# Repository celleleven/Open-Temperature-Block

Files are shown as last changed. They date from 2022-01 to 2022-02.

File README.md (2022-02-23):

<p align="center">
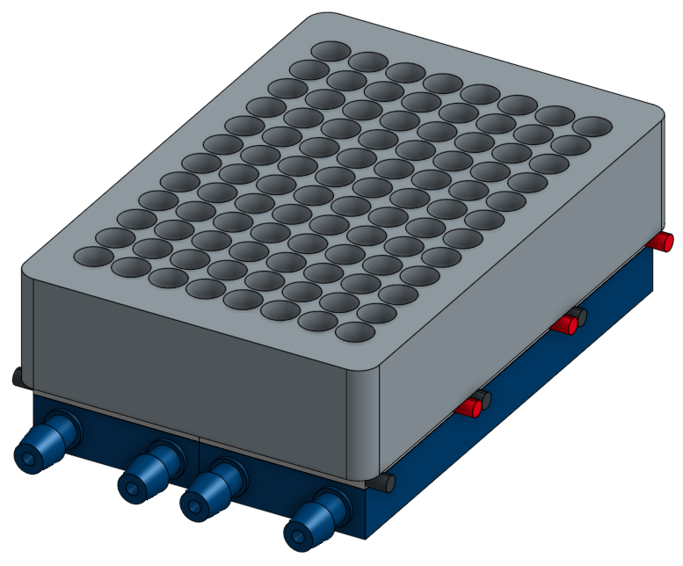
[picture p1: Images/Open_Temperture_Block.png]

</p>

# Open Temperature Block

_**TL;DR**_ This guide shows the process for engineering, fabrication, and operating of the OTB (Open Temperature Block).  The OTB is a bench tool for controlling the temperature of DIY biological experiments to include and is not limited to PCR, heat shock, hibernation, and incubation.  

### Background

## Engineering Design Process

	1.	Define the Problem:

The goal is to create a DIY, open-source, heating and cooling device for use in biological experiments.  The DIY portion of this device will be assembled using basic tools. Being open-source allows for revision, evolution, and free dissemination.  The heating control will allow for PCR reactions, heat shock experiments, incubation, and hibernation.

	2.	Identify Constraints:

| Name | Parameters |
| ----- | -----|
| Size | Microplate footprint (127.76 mm x 85.48 mm)|
| Weight | For shipping lighter is better |
| Cost | < $1000 USD (Competitor range: $900 <-> $20K, Average $5k )
| Power | 120VAC and 240VAC input
| Temperature Range |  ≤ 3°C to ≥ 100°C for a duration of < 30 Minutes |
|Componets| Readily sourced; electronics, hardware, microcontroller|
| Decibels | 60 decibels
| Water Tight | Does not leak
| Geometry | Rectangular
| Cleanability | Allows for cleaning.
| Assembly | Uses standard hex screws.

	3.	Brainstorm:

  | Idea | Pro | Con |
  | ----- | -----| ----- |
  |Peltier (TEC)| Cost-effective, heats and cools, small size| Uses a lot of power to remove heat.
  |Heat Element| Cost-effective, any size filament|  Doesn't cool
  |Compressor heat exchanger|Power Efficient|Expensive, Slow, not DIY.

	4.	Select promising solution:

The engineered solution will use a Thermal Electric Cooler (TEC) and a heat exchanger.  To create the OTB there will be three systems; power, data, and water-heat.

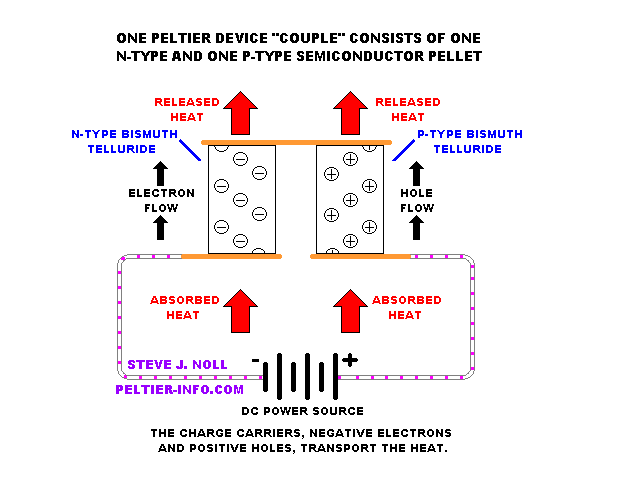
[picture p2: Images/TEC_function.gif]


The OTB is powered by a 12V 17AMP power supply. This will power the Peltier, fans, pump, and a voltage regulator will step down the 12V to 5V for the microcontroller.

The OTB data system is broken into device logic and external control. Device logic describes the microcontroller interaction with the Peltier, Temperature Probes, input devices. To accurately control the Peltier the microcontroller supplies a PWM signal to the high-power motor controller. This will change the electrical duty cycle allowing for precise Peltier control. The microcontroller samples temperatures from two thermistors.  One thermistor is located on the heat block and the other is attached to the heat exchanger.  These values will provide the logic needed to safely control the heat and cooling operations. External control consists of an I2C slave data line, display with buttons, and Wifi. The I2C data line allows for sending and receiving data from a Master I2C device. The display consists of an OLED display and four buttons.  The OLED in conjunction with the buttons allows the user to navigate through menus, and execute functions. Lastly, the Wifi provides a wireless gateway to Communicate with the OTB via a web page and RESTapi.

The water-heat system consists of a water block, pump, fan, and radiator.  In the heating phase, the microcontroller sends positive voltage to the Peltier.  In the cooling phase, the microcontroller sends a negative voltage to the Peltier.  Durning all heating and cooling operations the pump is moving water through the water block, through the tubing, to the radiator, and back to the water block.  The radiator uses an electric fan to blow air over the fins and exchange heat to the environment.

**Sketch (Free Body Diagram):**

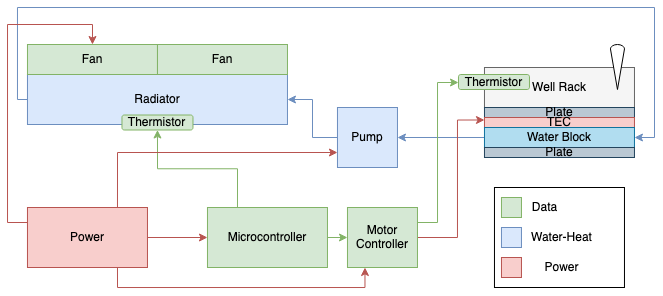
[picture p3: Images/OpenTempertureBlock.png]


<br><br>
MATH:

<!--
I have a circular track on this track there is a mine-cart.  The mine-cart picks up a payload (ore) at the vein.  The payload moves to the collector are emptied and repeats.  The mine-cart has a continuous speed around the track.  There is a rate the ore can be loaded into the mine cart, and there is a rate the ore can be removed to the collector.

If I cut the track in half, and start at the vein.
-->

	5.	Prototype

### Temperture Block
 <br>Parametric Model.

 <br>Version 1<br>

### Heat Exchanger and Power Train
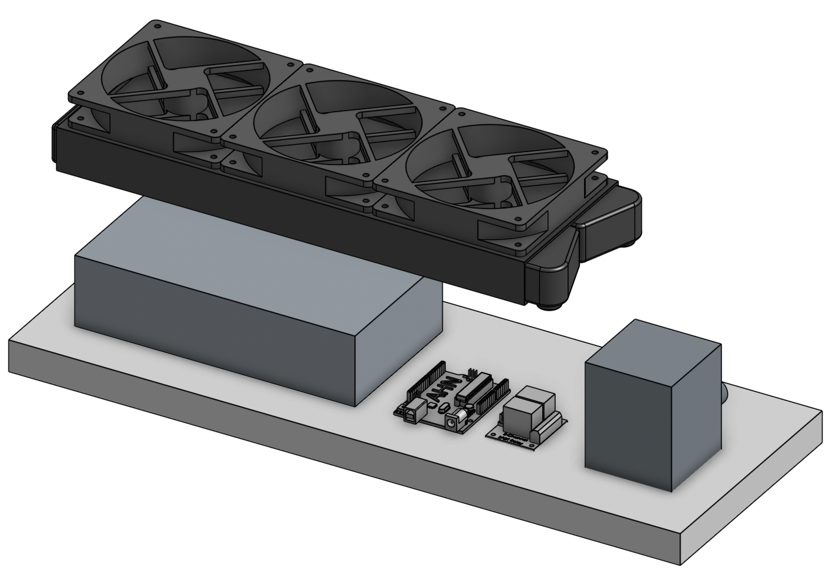
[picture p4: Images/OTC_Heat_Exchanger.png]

<br>Parametric Model.<br>


<br>Version 1<br>

### Logic Controller


<br>Version 1<br>

### Software Interface

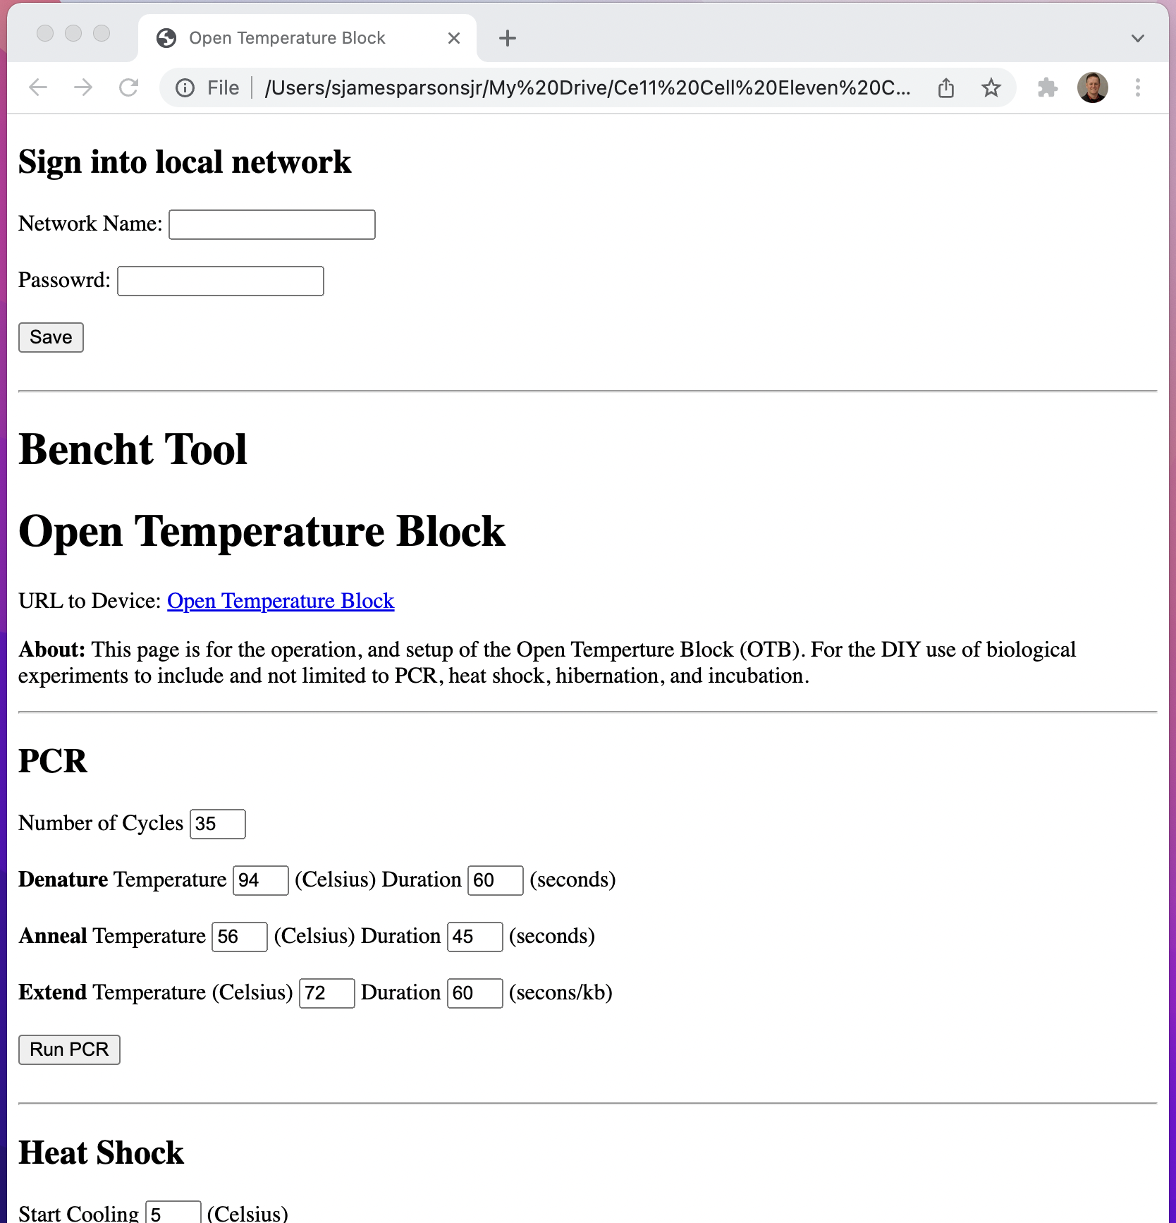
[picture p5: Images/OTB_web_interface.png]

<br>Version 1<br>

	6.	Test

### PCR Test Over 35 Cycles
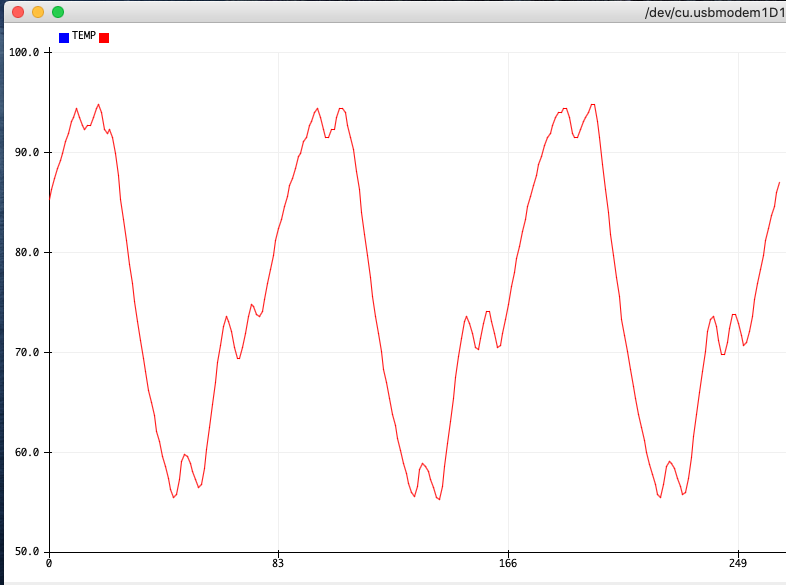
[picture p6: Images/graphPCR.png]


	7.	Iterate

	8.	Communicate Results.

### Support Websites
<!---[Buy Open Source Open_Temperture_Block](https://www.celleleven.com/product/Open_Temperture_Block/)
--->
## Hardware
| QTY | Name | Quantity | Cost | Item Cost | Total Cost | URL |
| --- | --- | --- | --- | --- | --- | --- |
| 6 | Peltier | 10 | 28.99 | 2.899 | 17.394 | https://amzn.to/3pDVF7H |
| 2 | 120x40 Water Cooling Block | 2 | 18.99 | 9.495 | 18.99 | https://amzn.to/3pyl8zk |
| 1 | 96 Well Aluminum Block | 1 | 169.13 | 169.13 | 169.13 | https://amzn.to/3DyzIvE |
| 1 | 24 Well Aluminum Block | 1 | 71.89 | 71.89 | 71.89 | https://amzn.to/3dthdhx |
| 1 | 384 Well Aluminum Block | 1 | 0 | 0 | 0 |  |
| 3 | Thermistors | 10 | 13.99 | 1.399 | 4.197 | https://amzn.to/3IsNvaJ |
| 1 | Wifi Microcontroller | 1 | 44.61 | 44.61 | 44.61 | https://amzn.to/3lIX8YV |
| 1 | 240x360 Radator | 1 | 29.99 | 29.99 | 29.99 | https://amzn.to/3duD08s |
| 3 | 120 Fan | 4 | 17.99 | 4.4975 | 13.4925 | https://amzn.to/2LkDNhD |
| 1 | 2 Relay Module | 4 | 8.99 | 2.2475 | 2.2475 | https://amzn.to/3rHmMkP |
| 6 | Vinyl Tubbing | 50 | 26.99 | 0.5398 | 3.24| https://amzn.to/3pyTouq |
| 8 | Hose clamps | 25 | 10 | 0.4 | 3.2 | https://amzn.to/3lLbY14 |
| 1 | Pump | 1 | 37.79 | 37.79 | 37.79 | https://amzn.to/3y0tPpT |
| 1 | Power Supply | 1 | 28.99 | 28.99 | 28.99 | https://amzn.to/3dsQ0LN |
| 0 | Stand Offs | 1 | 0 | 0 | 0 |  |
| 1 | Case | 1 | 60 | 60 | 60 |  |
| 6 | 12G Copper wire | 25 | 36.66 | 1.4664 | 8.80 | https://amzn.to/3lL9YpA |
| 4 | G1/4 Thread Soft Tube Barb | 6 | 11.15 | 1.86 | 7.43 | https://amzn.to/3pxsC5G |
| 1 | Ardunio PCB Board | 1 | 10.99 | 10.99 | 10.99 | https://amzn.to/3pyTouq |
| 1 | Real Time Clock (RTC) | 5 | 17.49 | 3.50 | 3.50 | https://amzn.to/3IfnBqF |
| 1 | DC-DC Buck | 1 | 30 | 30 | 30 | https://amzn.to/3Gn74iR |

 **Total** $565.88

 ## Fabrication

## Assembly
### Software
This Sequence Diagram outlines the functions needed for the OTB.

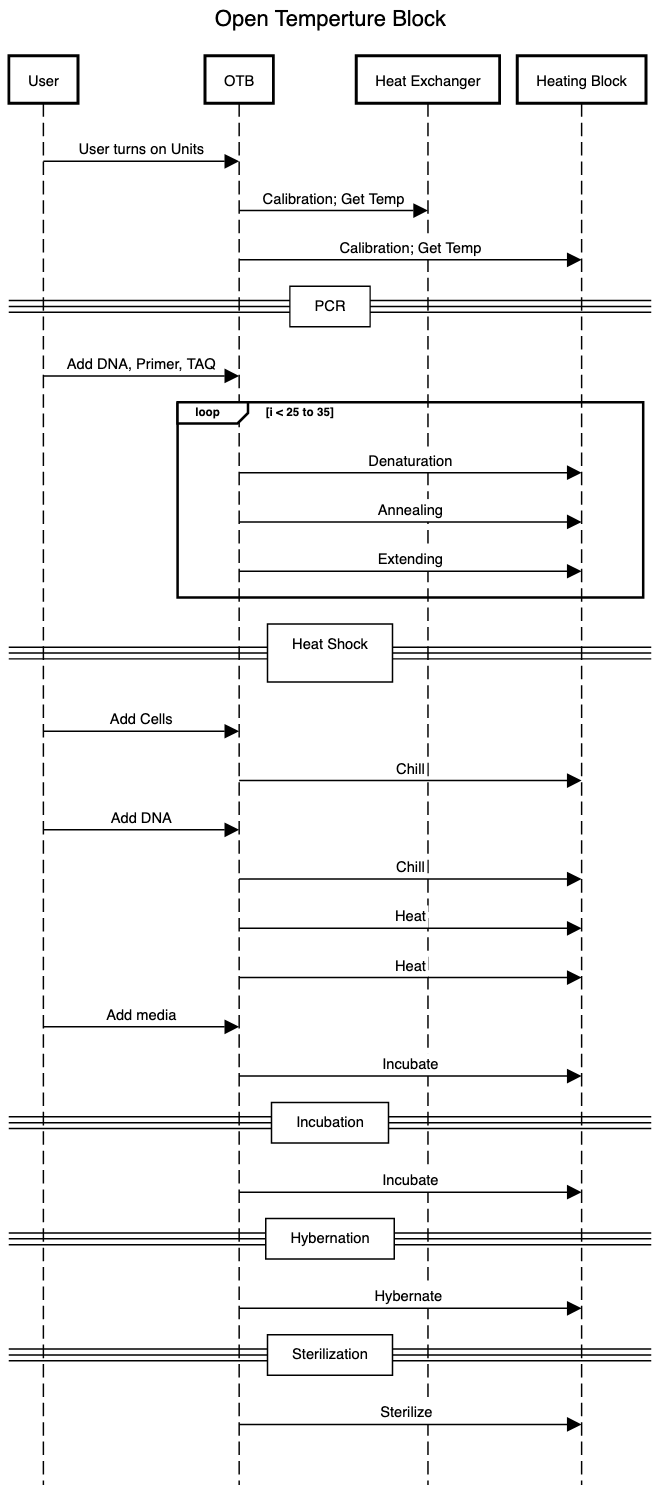
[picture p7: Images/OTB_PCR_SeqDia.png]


1. [Download Arduino IDE](https://www.arduino.cc/en/main/software)
2. Download this Zip File to your computer
3. Navigate to the ``Open_Temperture_Block Code`` folder
4. Upload Open_Temperture_Block.ino Code to Arduino

### Electronics
1. Solder wires and components onto Arduino Sheild PCB
2. Solder OLED, (4) Buttons, Wires, and JST-XHP connector to PCB
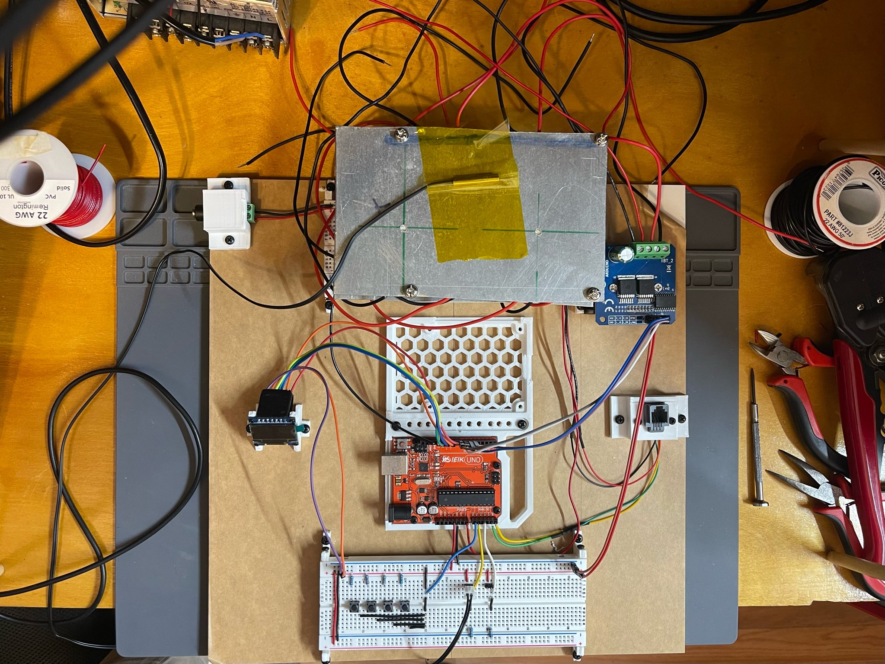
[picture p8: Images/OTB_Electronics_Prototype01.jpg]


### Case
1. [Laser Cut or 3D Print Frame gcode]()

### Hardware
1. Affix fan to the radiator.
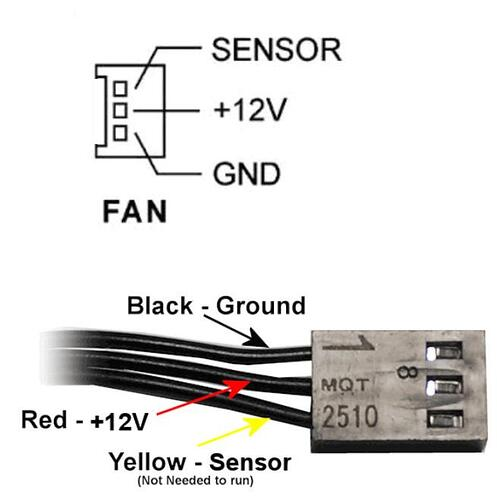
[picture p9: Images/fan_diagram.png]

2. Affix power supply, microcontroller, motor controller, pump, radiator to the base with screws
3. Fit RJ-11 Plug into housing.
4. Attach shield to the microcontroller and connect JST-XHP wires to shield
5. Assemble heating block.
<br>...
<br>...
<br>...
<br>...

## Directions

## Trouble Shooting

## Authors

* **[S James Parsons Jr](https://www.linkedin.com/in/sjamesparsonsjr/)**

## Purchase
<!--
[![Donation](https://i1.wp.com/calumetartcenter.com/wp-content/uploads/2013/02/paypal-buy-now-button.png?fit=284%2C136&ssl=1)](https://i1.wp.com/calumetartcenter.com/wp-content/uploads/2013/02/paypal-buy-now-button.png?fit=284%2C136&ssl=1)
-->

## License

This project is licensed under the MIT License - see the [LICENSE.md](LICENSE.md) file for details

<!--

Electronics

Wire Arduino Uno with dashboard circuit, RJ11 port, two thermistors, ~~Ultra sonic Sensor~~ BTS7960, fan, and water pump.

Wire Peltier's to DTS7960 and 12VAC power supply to the circuit.

Physically validate wires are correctly installed using a voltmeter to verify continuity.  

If no shorts, power the circuit.

Physically validate wires contain the correct voltage using the voltmeter starting at the source.

Power down circuit.

Coding

1. Using Arduino IDE / Wokwi.com, install all libraries, define all pin variables, initialize starting variable with values. Install dash and I2C functions.

2. Code the setup script. Debug any errors.

3. Code the thermistor function. Debug any errors. Upload to Arduino and calibrate.  Repeat previous steps for the second thermistor.   

4. Code the DTS7960 function. Debug any errors.

5. Code the fan function.

6. Code the Pump

Heating Block

1. 3D Print Mockups holder.
2. Fabricate heat transfer plate; Mark dimensions, oil, cut, clean, and deburr.
3. Tape plates together, drill and tap four 4mm holes for screws, deburr, and clean.
4. Assemble block by stacking bottom plate, water block, Peltier, and top plate and screwing together, being cautious not to crack the TEC units.  **NOTE: Should I use Thermal Paste?**
5. Attach plastic tubbing.  Using a razor blade cut two long pieces of PVC tubing (xx mm) length and 1 short piece of PVC tubing (xx mm) in length. Attach a short piece on the inner two barbs of the heating block. **NOTE: Do this before assembly, unless barbs are easy to access**
6. Wire management, using zip ties align the Peltier wires in the same direction as the PVC tubes.
7. Tin TEC wires and power wires.  Add heat shrink to all TEC wires. Crimp-on ring connectors to 12 TEC wires and two power wires.  Connect all rings using a nut and bolt. Heat shrink terminal junction.

# NOTE
**Material**
Melting	Conductivity
Aluminum 1221  239
Lead 621.5 34.7
Steel 2500 45
Copper 1984 397
Bismuth 520 7.97
PLA	180 0.13
Gallium 29.7 40.6
-->

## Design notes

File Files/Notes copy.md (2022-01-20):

2022/01/17

Open Heat Block

1. Wired two thermistors in a voltage divider configuration using a 10kΩ
2. Wired BTS7960 High Power Motor Driver to Arduino and power supply.
- *NOTE* TEC has a 5 AMP max.
- [ ] Need high power wire, the current wire is only rated for .98 AMPs.
3. Using Kapton tape attached thermistor one to heat block.
4. Code thermistor reading function.
5. Code BTS7960 High Power Motor Driver Function.
- Map() // Voltage (0 to 12) to PWM (0-255)
6. Merge thermistor code with BTS7960 code.

2022/01/18

Open Heat Block

1. Finish Sequence Diagram
2. Work on GitHub
3.

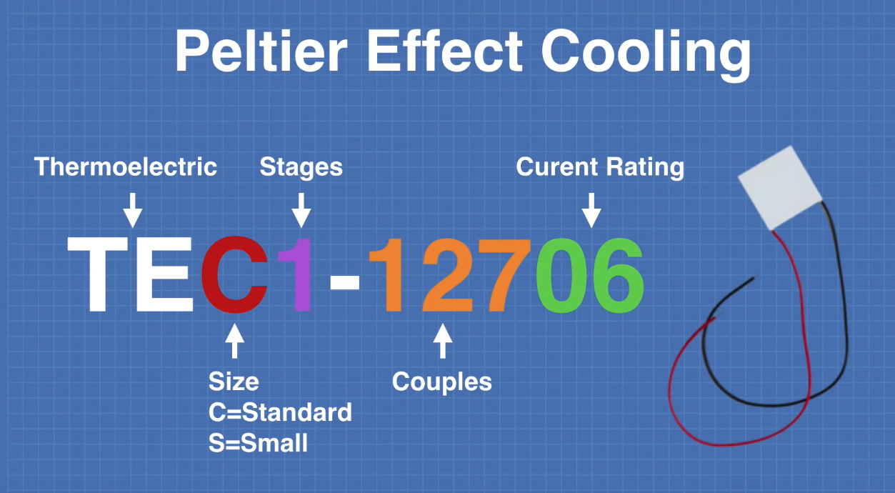
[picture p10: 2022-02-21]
Images/PeltierDesignator_DroneBotWorkshop.png

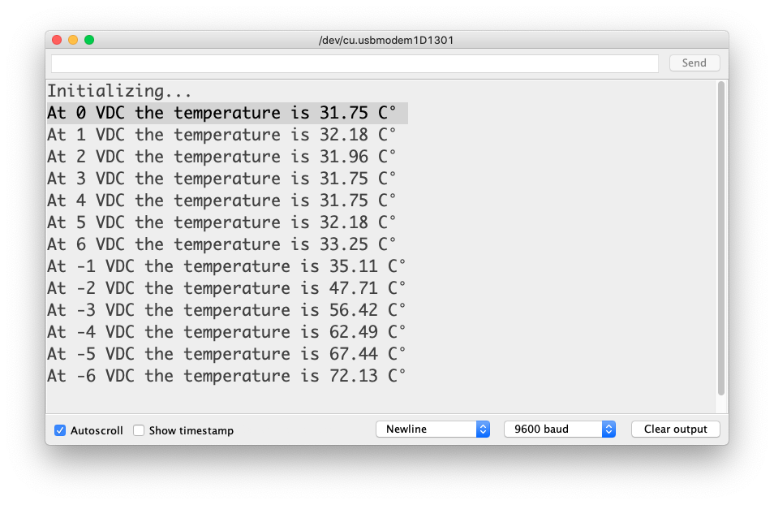
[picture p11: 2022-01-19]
Images/OTC_DeltaT60sec.png

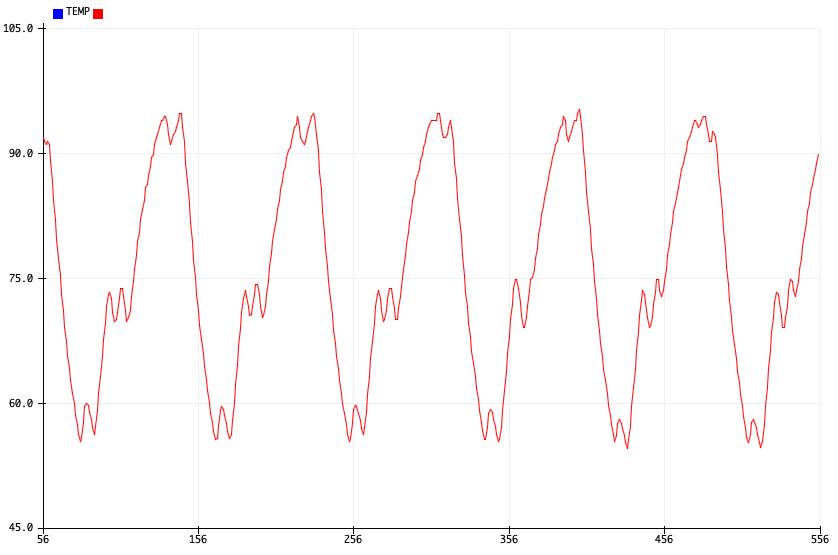
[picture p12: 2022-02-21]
Images/PCRCycle.png

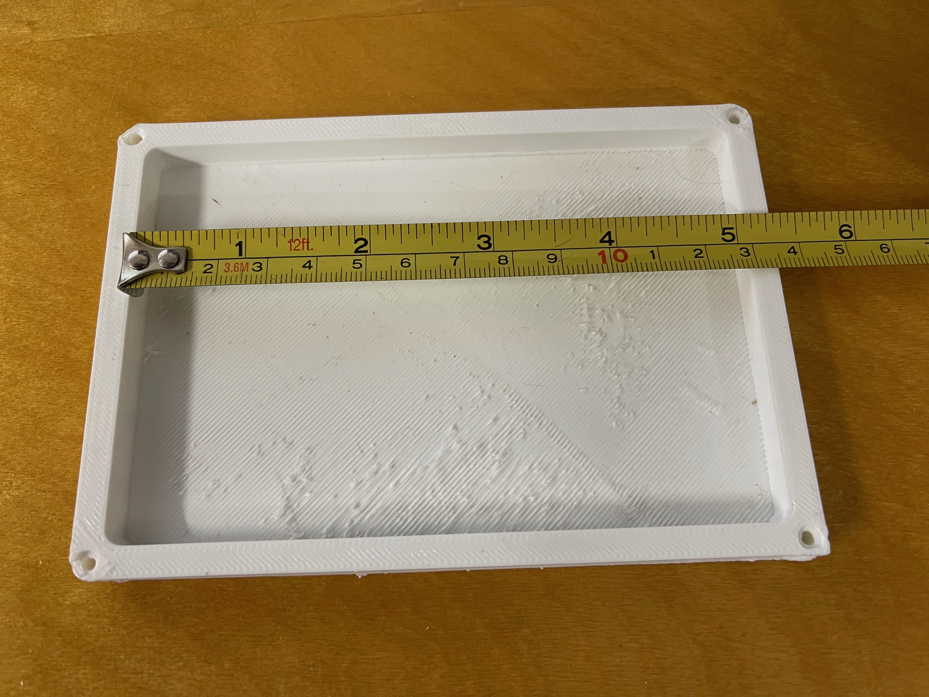
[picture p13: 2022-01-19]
Images/MicroPlate_mockup.jpg

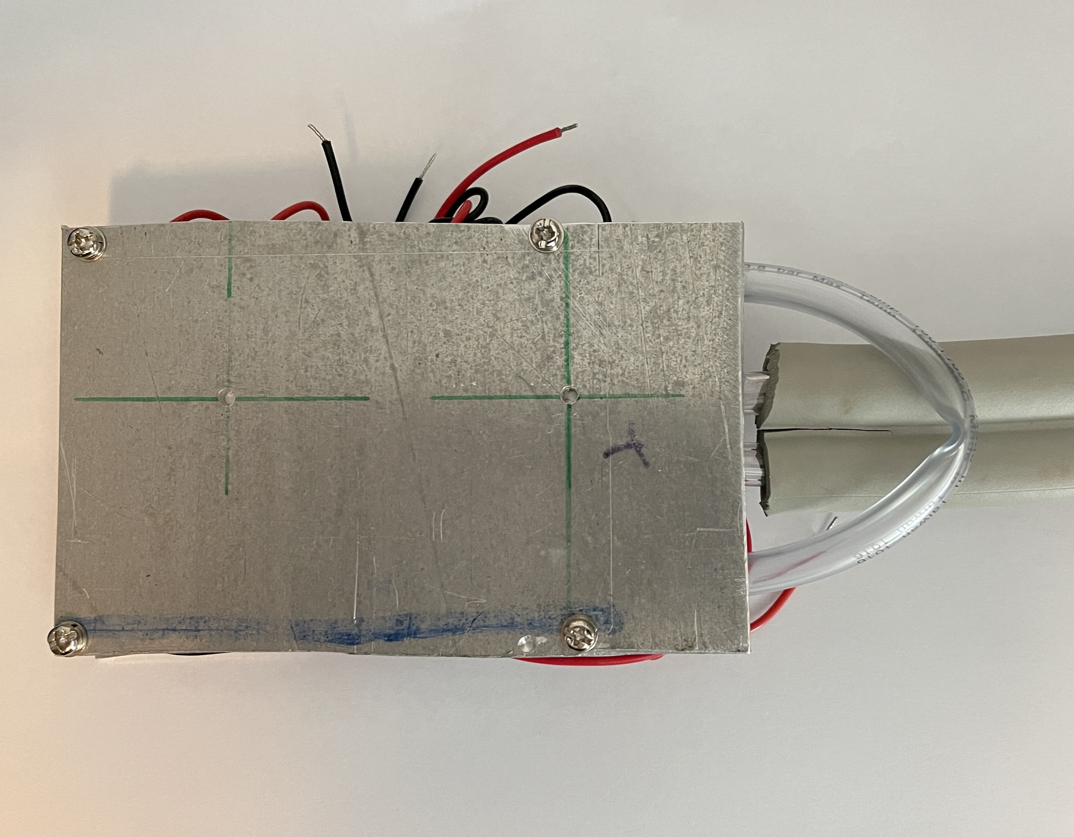
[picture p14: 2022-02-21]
Images/OT_Block_002.jpg

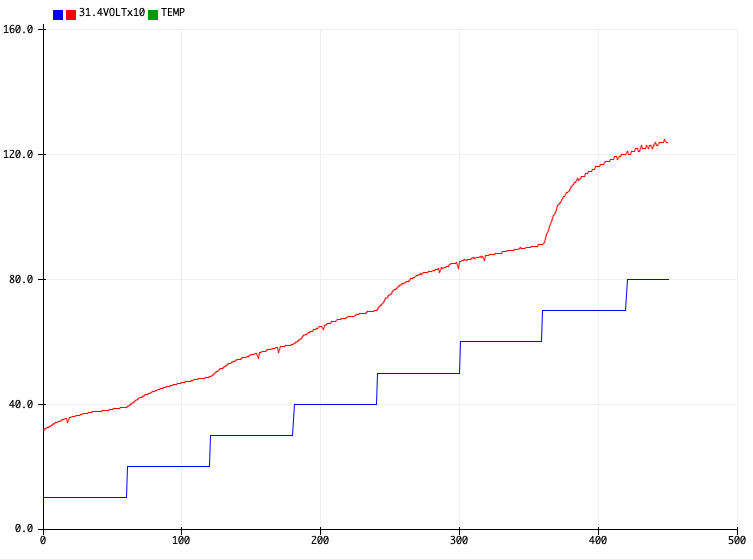
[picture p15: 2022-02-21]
Images/voltageVsTemp5min.png

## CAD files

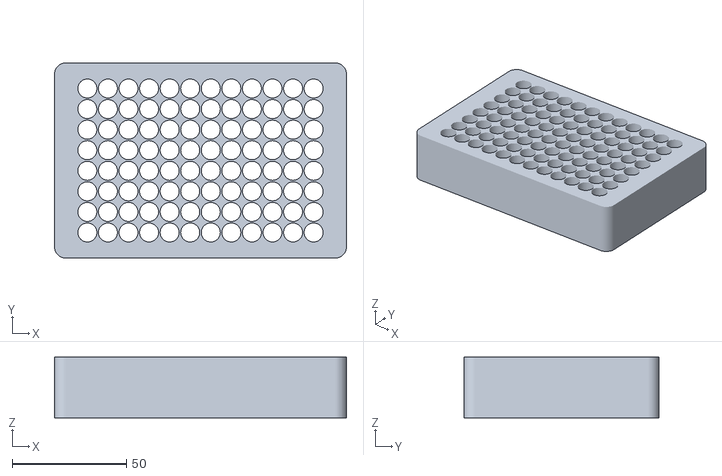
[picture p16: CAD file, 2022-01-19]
Images/96blockk.stl
127.8 x 85.5 x 26.5

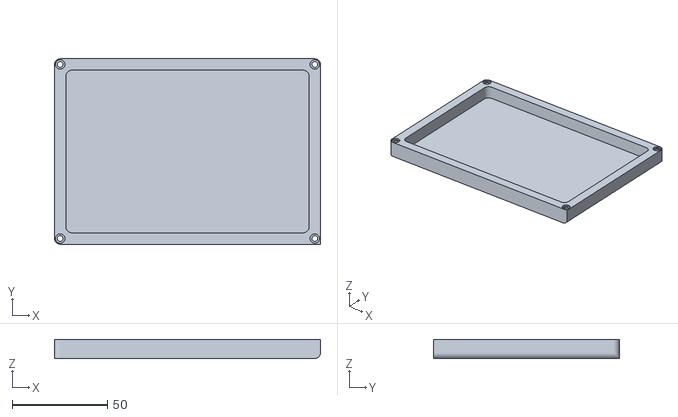
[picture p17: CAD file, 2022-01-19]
STL/Microplate.stl
139.8 x 97.5 x 10.0

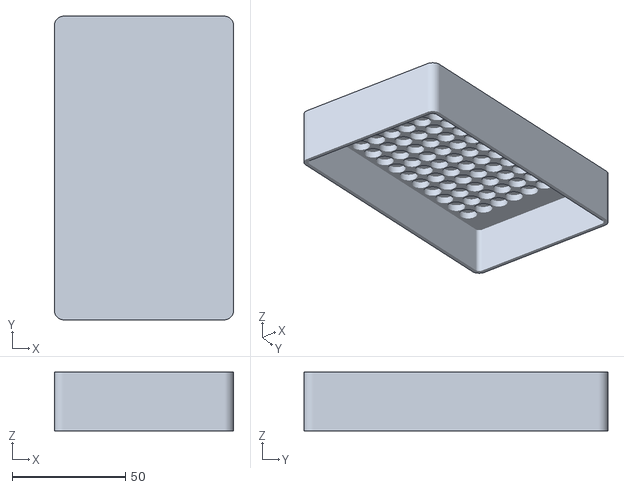
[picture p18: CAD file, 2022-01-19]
STL/BreadPan Insert.stl
79.0 x 134.0 x 26.0

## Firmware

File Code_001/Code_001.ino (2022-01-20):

//-------------------------------------------------------------------------
// 2022/01/17
//
// S James Parsons Jr
// www.sjamesparsonsjr.com
//
//-------------------------------------------------------------------------
//Device Specs.
//Name: BTS7960 Power Motor Dirver
//Buy URL = https://amz.run/5EVI
//Price = $8.99/2pcs = $4.50pcs
//Power = 5V [VDC]
//Date = 22/01/17 10:50:39 AM
//Code URL =

/*
   Notes:
*/


//-------------------------------------------------------------------------
// +++ Libraries +++


//-------------------------------------------------------------------------
// +++ Variables +++
#define RPWM 5 // BLUE Wire
#define LPWM 6 // PURPLE Wire
#define REN 7 // GREY Wire
#define LEN 8 // WHITE Wire

#define LED_BUILTIN 13 // LED

#define ThermistorPin A1 //  Yellow wire

int Vo;                             // Thermistors variables
float R1 = 10190;                   // Thermistor voltage divider resistor value
float logR2, R2, T, Tc, Tf;         // Variables for Thermistor
float c1 = 1.009249522e-03, c2 = 2.378405444e-04, c3 = 2.019202697e-07;

//-------------------------------------------------------------------------

int Temperature() {
  Vo = analogRead(ThermistorPin);                             // Get V_out from analong data pin A1
  R2 = R1 * (1023.0 / (float)Vo - 1.0);                       // Solve for Thermistor resistance using voltage devider formula
  logR2 = log(R2);                                            // Log or R2 for the Steinhart-Hart equation
  T = (1.0 / (c1 + c2 * logR2 + c3 * logR2 * logR2 * logR2)); // Steinhart–Hart equation resistance to Kelvin formula
  Tc = T - 273.15;                                            //Convert Kelvin temp to Celsius
  return Tc;
}

//-------------------------------------------------------------------------
// +++ Setup +++
void setup() {
  // put your setup code here, to run once:
  Serial.begin(9600);
  pinMode(RPWM, OUTPUT);
  pinMode(LPWM, OUTPUT);
  pinMode(LEN, OUTPUT);
  pinMode(REN, OUTPUT);
  digitalWrite(REN, HIGH);
  digitalWrite(LEN, HIGH);
  Serial.println("Initializing...");
}

//-------------------------------------------------------------------------
// +++ Loop +++
void loop() {
  bool Heating = HIGH;
  Temperature(); // Gets thermistors current temperture
  if (Tc < 90 && Heating == HIGH) {
    analogWrite(RPWM, 255 );
    analogWrite(LPWM, 0);
    Serial.print("Temperture = ");
    Serial.println(Tc);
  }
  if (Tc == 90) {
    Heating = LOW;
    analogWrite(RPWM, 0);
    analogWrite(LPWM, 0);
  }
}

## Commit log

2022-01-19 Update
    Added data
    [96blockk.stl, BreadPan Insert.stl, Microplate.stl, PCR_OTB.fzz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]
2022-01-20 Update file structure
    Added files to folders, cleaned up the read me file
    [PCR_OTB.fzz, PCR_OTB2.fzz]
